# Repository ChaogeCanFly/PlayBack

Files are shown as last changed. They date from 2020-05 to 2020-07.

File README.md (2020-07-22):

# Augmented reality System - Playback
The study of bats requires the ability to record and generate sound waves in the ultrasonic ranges. The required bandwidth for such systems is up to 100kHz, which is much higher than the common acoustic systems designed for humans. Studying bat echolocation capabilities and generating real time acoustic responses requires a minimal latency acoustic system. The few available systems on the market aren`t designed for real time signal processing and manipulation. In order to meet those constrains, a full acoustic system was developed. The system includes a Smart microphone module embedded with a microprocessor, a Speaker-amplifier and a Switch box which is capable of signal redirection and real time processing.
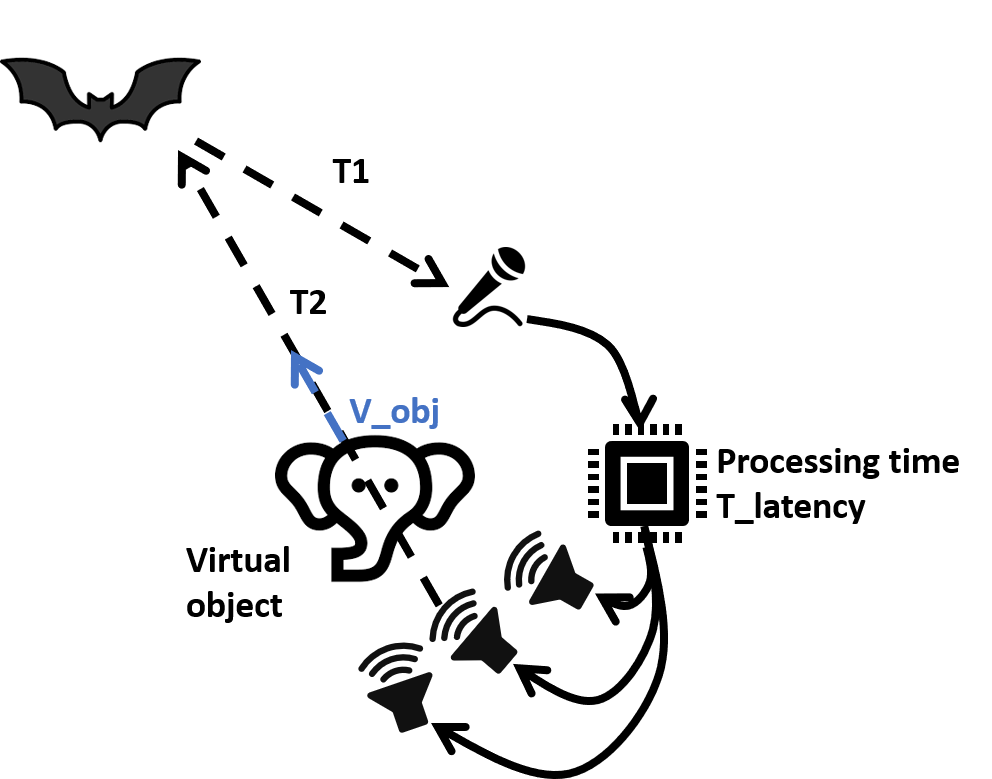
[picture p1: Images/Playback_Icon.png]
Augmented reality illustration

 
## PlayBack
The PlayBack setup consists of three main modules: Smart Microphones, a Switch and speaker amplifiers.  It is designed to monitor audio signals from multiple microphone modules and direct a signal from a selected microphone to an array of speaker modules including DSP options for audio processing in real time. The setup is designed to work at an audio bandwidth of 1-100 kHz at up to 1MS/S.
 
 ### 3d Models:
The casings for the modules have been designed in Fusion 360 and 3d printed
[Microphone](https://a360.co/2HDuYLZ)
[Switch](https://a360.co/36yYfSj)
[Amplifier](https://a360.co/2WX1Lmh)

### System Diagram
The system’s topology is such that the microphone modules are connected to the switch module using a standard RJ25 cable. The 6 wires of the cable are used to pass the following between the Smart microphones and the Switch: power to the module, trigger signal, the audio signal and an analog “quality” signal. The Switch module consists of two MCU`s (Micro Controller Unit), one is used as the Switch interface, and routes the signals while the other is used as a DSP MCU to implement signal processing in real time to the acoustic signal. The speaker amplifiers are connected through an RJ45 cable which in turn is used to supply power from the switch to the amplifiers and transmit the audio signals and the enable signal to the amplifier. The Switch module is connected to a Matlab GUI application running on a PC using an Xbee adapter for wireless operation. In addition, a Saleae logic analyzer is connected to the Switch allowing to monitor the analog signals and the trigger signal.
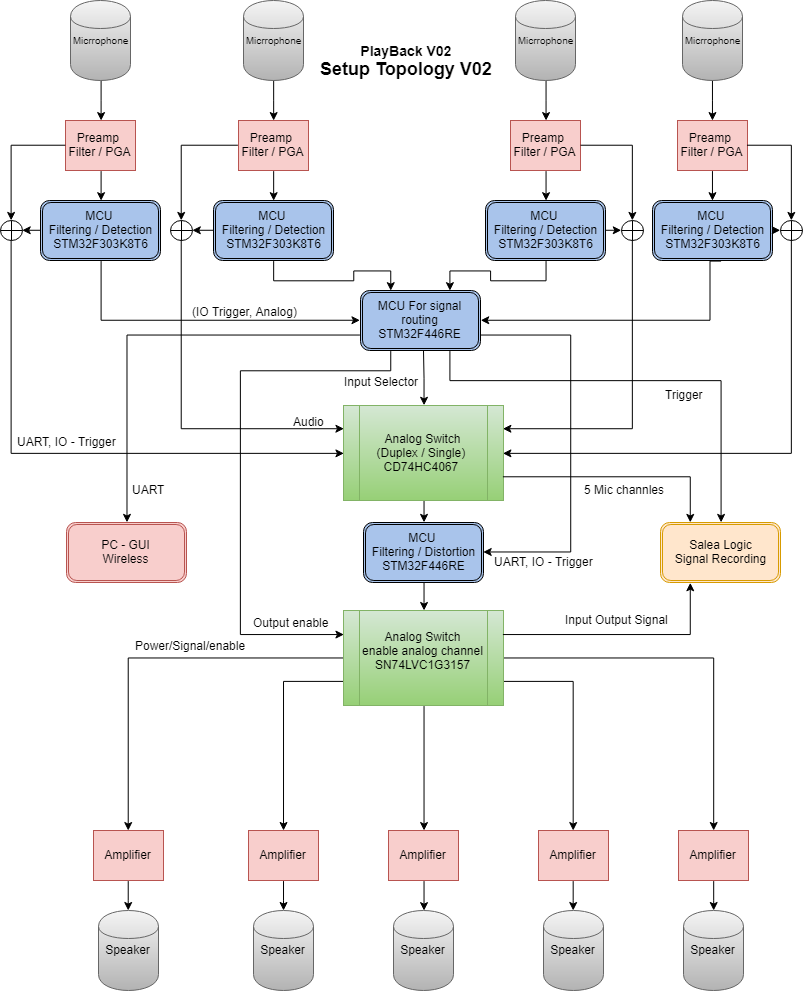
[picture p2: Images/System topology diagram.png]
System Diagram

 
### Smart Microphone
The Smart microphone module is designed to meet the required acoustic bandwidth of bat echolocation calls. In addition, since the system requirements are minimal latency for signal processing and signal manipulation, each of the microphones are embedded with a dedicated microprocessor which is responsible for the initial signal processing of the individual acoustic source. Such an approach allows spreading the computational power required by the system and simplifies the decision-making requirements of the Switch by reducing the acoustic information to a more simplified representation of an acoustic source. i.e. digital triggers / signal quality indication. This approach also allows future expending of the system since each of the microphones acts as an independent entity responsible for its own acoustic system. Adding more microphone to a system will not influence the required signal processing for the main unit.
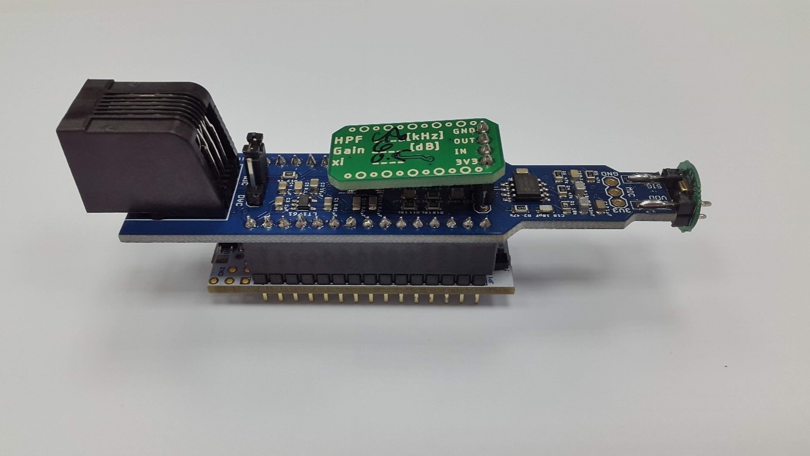
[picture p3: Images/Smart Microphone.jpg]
Smart Microphone


### Switch
The Switch Module is used as the center piece of the system. It connects all the Smart microphone modules and Speaker amplifiers, has an analog routing circuitry to route one of the microphone signals to several speakers. In addition, it acts as a power delivery system, converting a single supply source to several voltage levels for the various components of the system. The switch contains several status indicators such as active speaker LEDs, external trigger. Connectors for all the analog signals running through the system and generally configured status LEDs for future configurations. The switch module contains two MCUs, Switch MCU and DSP MCU, the Switch MCU is used as the system interface and responsible for routing the acoustic signals and monitor the trigger events from the Smart Microphones, while the DSP MCU is used as a DSP and implements various signal processing algorithms.
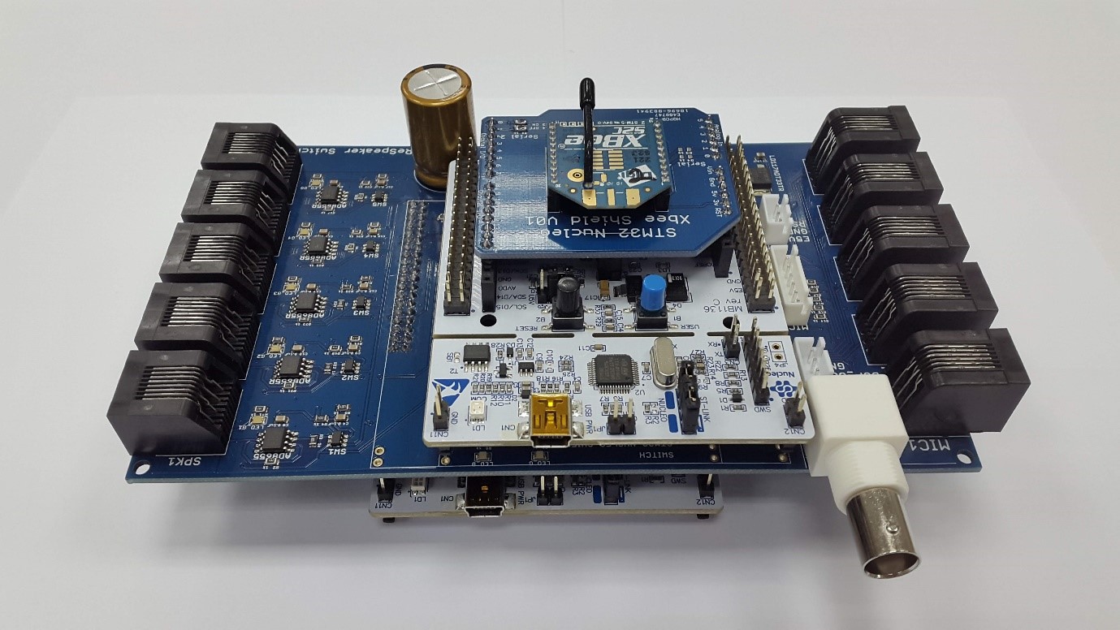
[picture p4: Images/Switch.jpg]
witch
 

### Speaker amplifier
Generating sounds in the ultrasonic frequencies (above 20kHz) requires a dedicated amplifier. Since commercial amplifiers are usually designed for the human hearing range and are commonly implemented through power efficient amplifiers (Class D). These speakers work as digital switches at high frequencies above the human hearing thresholds. The high frequency digital switching is converted to an analog signal using the natural low pass filtering characteristics of the speaker coils. The attempt to use such an amplifier at an ultrasonic frequency will result in high frequency distortions if any sound is generated at all since the common amplifiers are implemented with filters to cut the ultrasonic ranges from the input signals.
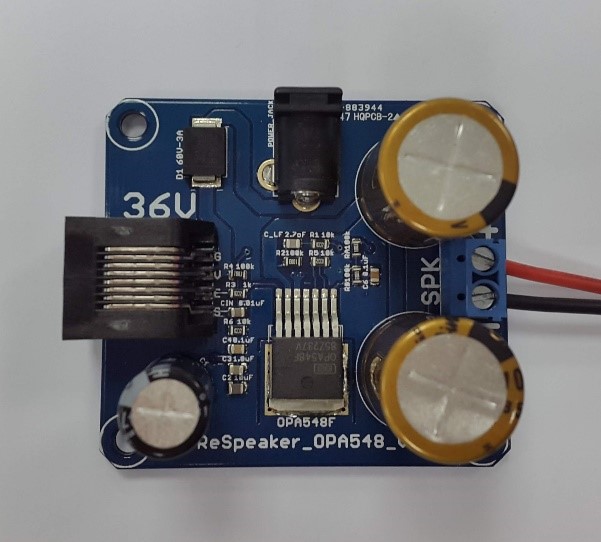
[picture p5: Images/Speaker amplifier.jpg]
Speaker amplifier
 

### GUI Microphone
To control the software parameters of the Smart Microphone, a GUI was created in Matlab. The Microphone has a UART communication over USB with the PC through the MCU`s micro USB connection or through an Xbee adapter board connected to its mate at the PC - as a wireless configuration. The GUI is designed with several section, Connection settings section, Parameters setting and display section, Messages section and Microphone updates section.
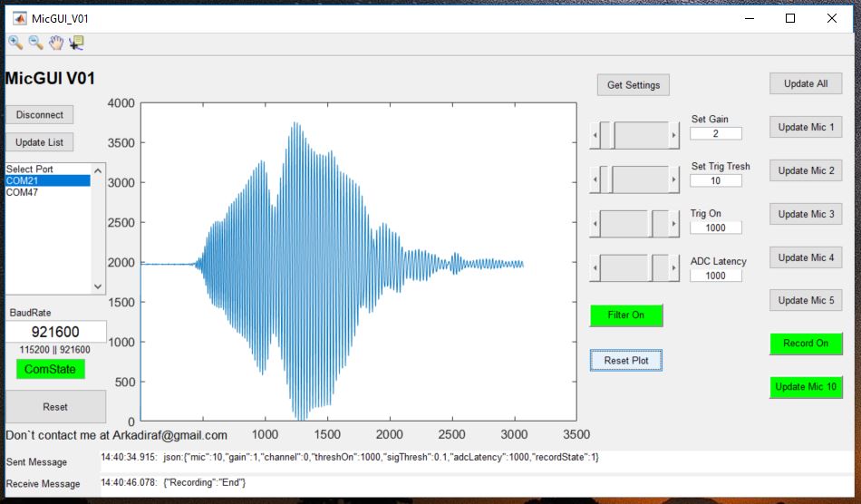
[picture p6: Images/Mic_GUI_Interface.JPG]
GUI Microphone


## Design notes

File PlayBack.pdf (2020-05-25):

# Augmented Reality System for bats based on Acoustic Signal Manipulation

The study of bats requires the ability to record and generate sound waves in the ultrasonic ranges. The required bandwidth for such systems is up to 100kHz, which is much higher than the common acoustic systems designed for humans. Studying bat echolocation capabilities and generating real time acoustic responses requires a minimal latency acoustic system. The few available systems on the market aren`t designed for real time signal processing and manipulation. In order to meet those constrains, a full acoustic system was developed. The system includes a Smart microphone module embedded with a microprocessor, a Speaker-amplifier and a Switch box which is capable of signal redirection and real time processing (Figure 1).

The proposed system in this study allows signal manipulation and processing at up to 1 MHz sample rate with a bandwidth of 1 – 100 kHz. The system is capable of monitoring up to 5 microphones and directing a selected sound source to up to 5 speakers for simultaneous transmission. Several experiments are presented demonstrating the systems capabilities for signal manipulations such as digital filtering, automatic triggering and signal rerouting, inducing latencies and variable gains. In addition, future developments will allow more complex applications such as a real time doppler effects.

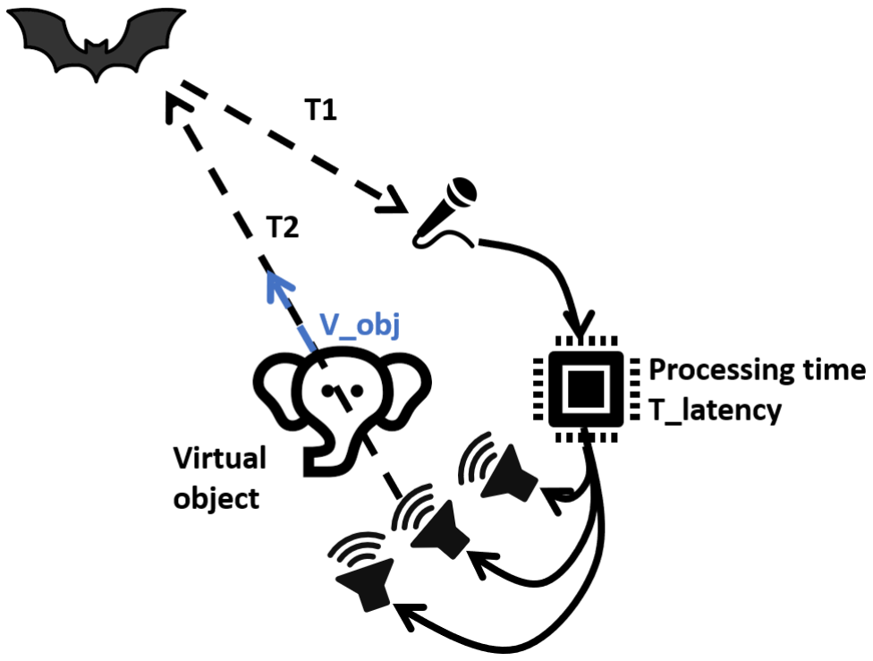
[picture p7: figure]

Figure 1. Augmented reality illustration: A bat call is received by a microphone, processed and transmitted through several speakers generating a virtual object to be perceived by a bat.

## 1 System Overview

The PlayBack setup consists of three main modules: Smart Microphones, a Switch and speaker amplifiers (Figure 2). It is designed to monitor audio signals from multiple microphone modules and direct a signal from a selected microphone to an array of speaker modules including DSP options for audio processing in real time. The setup is designed to work at an audio bandwidth of 1-100 kHz.

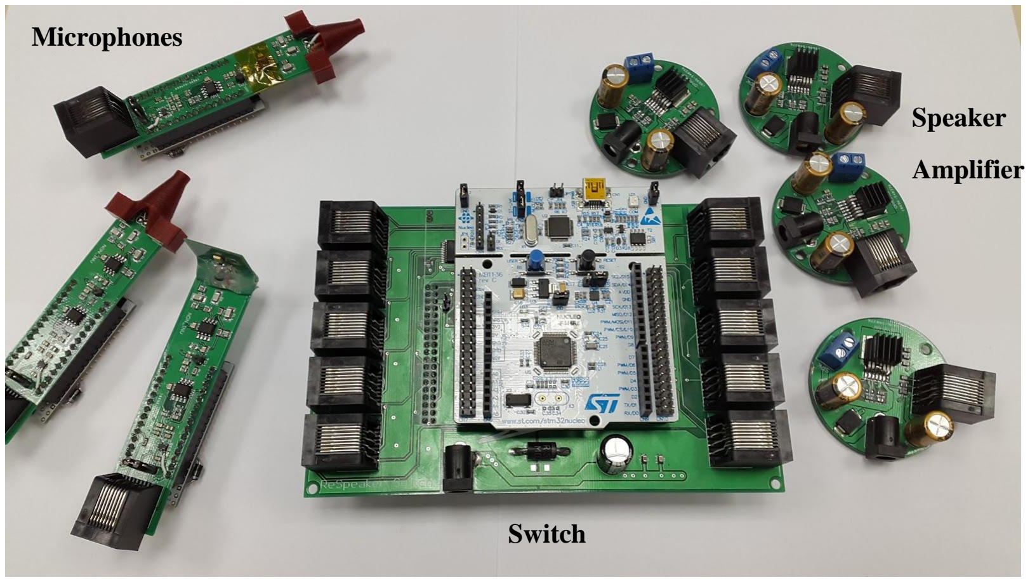
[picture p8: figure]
Microphones; Switch; Speaker; Amplifier

Figure 2. The Playback system – Smart Microphone on the left, Switch Module in the middle and Speaker amplifiers on the right.

The system’s topology (Figure 3) is such that the microphone modules are connected to the switch module using a standard RJ25 cable. The 6 wires of the cable are used to pass the following between the Smart microphones and the Switch: power to the module, trigger signal, the audio signal and an analog “quality” signal. The Switch module consists of two MCU`s (Micro Controller Unit), one is used as the Switch interface, and routes the signals while the other is used as a DSP MCU to implement signal processing in real time to the acoustic signal. The speaker amplifiers are connected through an RJ45 cable which in turn is used to supply power from the switch to the amplifiers and transmit the audio signals and the enable signal to the amplifier. The Switch module is connected to a Matlab GUI application running on a PC using an Xbee adapter for wireless operation. In addition, a Saleae logic analyzer is connected to the Switch allowing to monitor the analog signals and the trigger signal (Figure 4).

Figure 3. System topology diagram: An array of up to 5 microphone modules are connected to a switch module which connects to up to 5 speaker amplifier modules with ultrasonic speakers. The switch module is connected to a PC and the signals are monitored by a Saleae Logic analyzer.

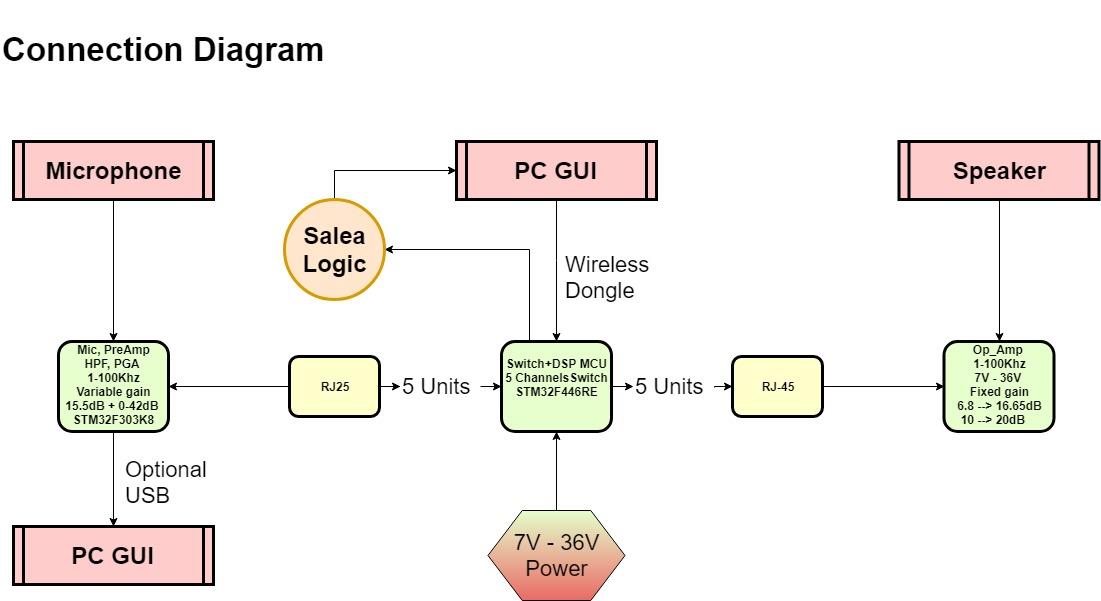
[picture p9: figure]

Figure 4. Playback System Connection diagram: Microphones connected through RJ25 cables to a switch module which is connected to speaker amplifiers through RJ-45 cables.

## 1.1 The smart microphone

The Smart microphone module (Figure 5) is designed to meet the required acoustic bandwidth of bat echolocation calls. In addition, since the system requirements are minimal latency for signal processing and signal manipulation, each of the microphones are embedded with a dedicated microprocessor which is responsible for the initial signal processing of the individual acoustic source. Such an approach allows spreading the computational power required by the system and simplifies the decision-making requirements of the Switch by reducing the acoustic information to a more simplified representation of an acoustic source. i.e. digital triggers / signal quality indication. This approach also allows future expending of the system since each of the microphones acts as an independent entity responsible for its own acoustic system. Adding more microphone to a system will not influence the required signal processing for the main unit.

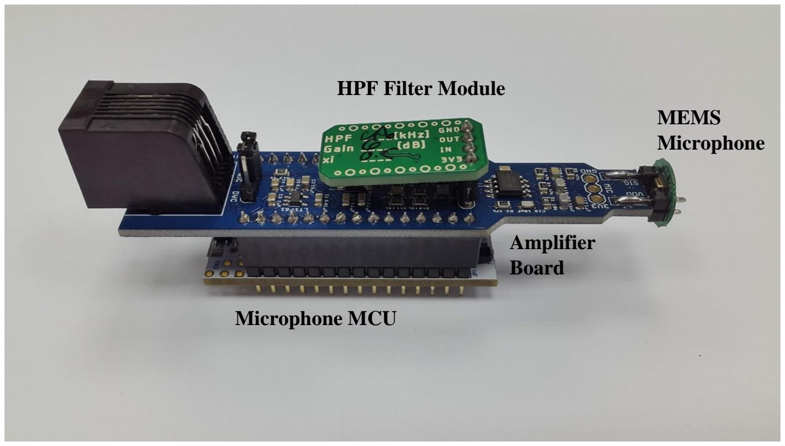
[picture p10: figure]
HPF Filter Module; Microphone MCU; MEMS Microphone; Amplifier Board

Figure 5. The Smart Microphone module: Round PCB populated with a mems microphone membrane, attached to an analog amplifier board (blue PCB). At the top attached an analog HPF filter module and at the button an MCU board.

### 1.1.1 Electronics

The Smart Microphone module is assembled by 4 independent electronic boards (Figure 5). The modules contain several parts, an analog mems membrane for the ultrasonic ranges and an analog amplifier board matched for the mems microphone. The amplifier board contains an adapter for an Analog high pass filter to allow the replacements of the board for various filter characteristics for the specific acoustic responses required. The whole system is mounted on a microcontroller board for signal detection and signal manipulation.

The circuit components were chosen to meet the system’s requirements of an audio bandwidth of 1-100kHz. The mems microphone (SPU0410LR5H) chosen for the design has an acoustic characteristic at up to 100kHz. The signal operational amplifiers (Op Amp`s)

chosen for the design are an AD8655 which is a low noise high bandwidth operational amplifier, with 28MHz bandwidth, capable of a single supply design and rail to rail signals. The programmable gain amplifier (PGA - PGA112) module has similar analog characteristics of 10MHz bandwidth, rail to rail signals and is compatible for single supply designs. In addition, the PGA has an internal MUX of 2 channels, allowing a digital selection of the signal source. The chosen PGA is cable of an additional amplification stage in binary stages from 1 to 128 gain. The main board 3V3 LDO regulator LT1761 is selected for its good noise rejection for the circuit`s analog bandwidth.

In order to work with an analog microphone a matching amplification circuit is implemented. The amplification circuit has several stages each selected and implemented for its individual purpose and are illustrated in Figure 6. The first stage contains an amplifier circuit at a non-inverting configuration with a gain of 15.1dB and is called a preamplifier. It`s purpose is to amplify the “weak” signals generated by an analog microphone. It is designed with a high impedance input to match the high impedances of the analog microphone. The amplification is selected to meet the full bandwidth of the microphone up to its saturation point. Following the preamplifier is an analog high pass filter module (HPF module). The analog high pass filter is implemented on a separated board in order to be easily replace by a different high pass filter module with different analog characteristics. Following the HPF module is a programmable gain amplifier (PGA). The PGA is configured digitally by the on board MCU and as an internal mux allowing the selection of a filtered signal from the HPF module or the unfiltered signal fed directly by the preamplifier. The PGA acts a variable gain amplifier and is implemented in order to amplify the signals to the full scale of the microprocessor’s ADC levels (analog to digital converter) by that utilizing the full resolution of the MCU ADC which is limited to 12bit. The amplifier board has a physical jumper which can select the output source for the acoustic signal. Either the generated signals by the MCU, or the analog signal of the PGA unit.

The HPF module for the setup is designed as a second order analog high pass filter at a cutoff frequency of 48kHz with a damping factor of 0.5 in addition it adds a 6dB gain to the signal respectively to the dumping factor, The design was evaluated using a Simulink simulation and evaluated based on preliminary recording for best performance at ultrasonic ranges of a bat callings.

The amplifier board is mounted on top of a microprocessor which samples the amplified signals of the PGA unit and generates an analog signal through its digital to analog converter (DAC) at 12bit resolution and up to 1 MHz sample rates. The MCU can delay the signals and detect signals presence by amplitude threshold evaluation. When a signal is present an IO interrupt is set to notify the switch of a present signal. The software parameters of the MCU are configured by a Matlab GUI (Figure 9, Figure 6).

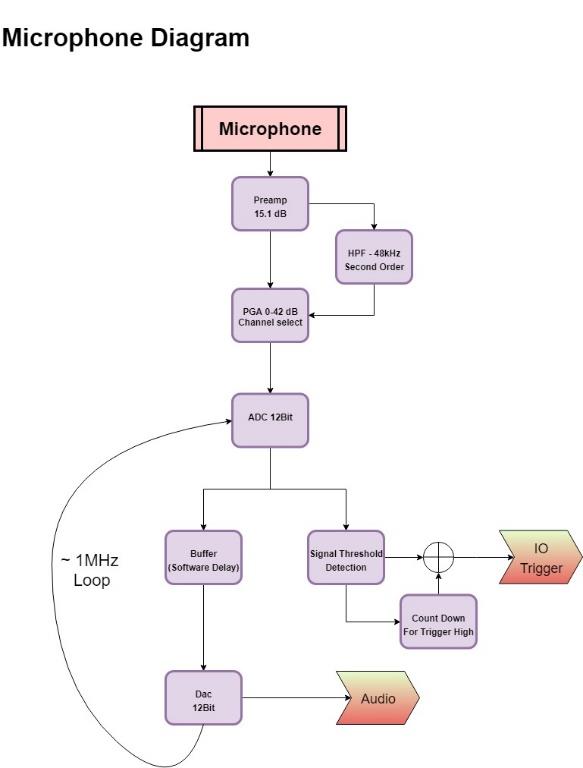
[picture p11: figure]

Figure 6. Smart Microphone diagram: Hardware & Software implementation diagram. Illustrated an amplifier circuit, with preamp, HPF and PGA implementation. Following sampling of the signal by a microcontroller, and software implementation for the sample. Signal detection, and delay implementation. With appropriate signal generation – i.e. Digital trigger and generated analog signal.

### 1.1.2 MCU code

The code for the Smart Microphone MCU (STM32F303) is implemented through an STM32CubeIDE environment, using C++ language. The MCU is responsible to the communication with the Matlab GUI and implements some signal processing in real time.

The main code algorithm is represented in Figure 6, The MCU performs an analog to digital conversion at 12 bits resolution (ADC), stores the sample into a circular buffer, checks if a bat signal is present by a simple threshold comparison to a stored variable, if a signal is present the MCU sets a trigger IO high to update the Switch MCU of a present signal and sets a countdown which ends with resetting the trigger IO state. A digital to analog conversion

(DAC) at 12 bits is than performed to a stored value in the circular buffer, defined by the set delay. The whole loop is performed at about 1MHz.

The communication with the Matlab GUI is done through a UART stream which triggers an interrupt routing in the MCU workflow. The incoming byte is checked for the correct values depending on the defined state for the transmission (Figure 7).

- State 1: compares the incoming byte to the defined header - failed comparison resets the buffer and transmission state
- State 2: stores the incoming bytes to a packet stream.
- State 3: compares the incoming byte to the defined footer - failed comparison resets the buffer and transmission state.

When a successful transmission is performed, the defined packet bytes are parsed in the format of a Json message. The variables are derived by the variable names and used to update the stored variables of the MCU in the virtual EEPROM memory of the MCU. The data exchange is completed by sending an acknowledgement message to the Matlab GUI, stating the microphone number using the Json format for message construction.

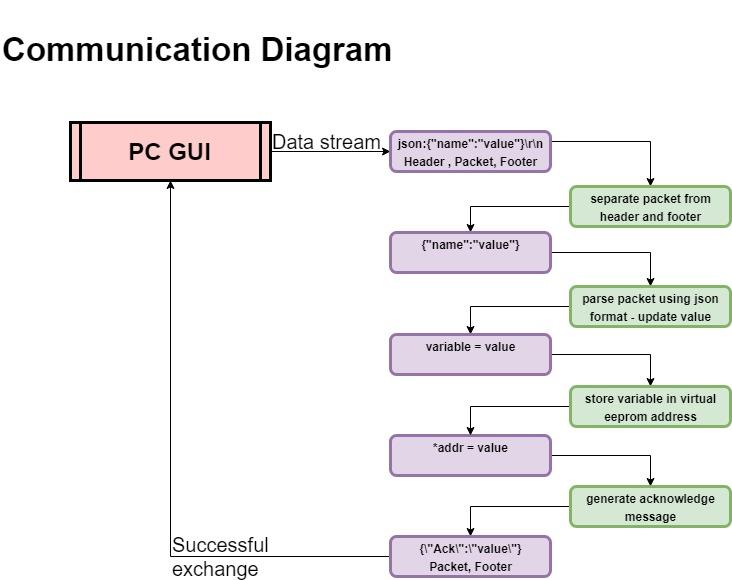
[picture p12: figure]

Figure 7. Smart Microphone communication diagram: The implementation of the communication protocols is based on packet handling and json formats.

Recoding of a signal is performed when a recording state is selected in the Matlab GUI. The transmission begins when a countdown for the trigger event is finished. The recorded signal is then transmitter in a binary form (Figure 8). Prior to sending the packet, an update is sent in a json format to notify the Matlab GUI of an upcoming binary packet, the size of the binary packet, and an index for the start of the circular buffer. The Matlab GUI is then switched to the binary packet retrieval state and the MCU sends the circular buffer in a binary format. After the binary packet is transmitted, the MCU sends a json message stating the end of a transmission and by that it acknowledges the Matlab GUI of a successful packet transfer. Using a binary format, reduces significantly the number of bytes required to be transmitted and the overhead for the communication protocol over UART, allowing a continuous capture of bat calls at up to 20 – 30 calls a second at a 3-4 ms duration each.

Figure 8. Binary packet transfer: Binary communication protocol allows large files with minimal bandwidth requirements, including an error detection mechanism implemented by a handshake implementation.

### 1.1.3 Matlab GUI

To control the software parameters of the Smart Microphone, a GUI was created in Matlab (Figure 9). The Microphone has a UART communication over USB with the PC through the MCU`s micro USB connection or through an Xbee adapter board connected to its mate at the PC - as a wireless configuration. The GUI is designed with several section, Connection settings section, Parameters setting and display section, Messages section and Microphone updates section.

The Matlab GUI buttons settings include:

Disconnect / Connect – Disconnect from currently connected USB COM Port. Or connect to the selected COM Port from the Select Port menu.

Update – Refreshes the Select Port menu with the available COM Ports connected to the MCU.

Select Port Menu – Displays the available COM Ports connected to the PC.

BaudRate – Baud Rate for the selected connection, for a Cable connection the configured baud rate is 921600, as for the wireless configuration it is 115200.

ComState – Displays the connection status with the MCU, Green if the connection is active, Red for an inactive connection.

Reset – Resets the GUI configuration and updates the MCU with the default configuration settings.

Sent Message – Displays the last sent messages to the MCU.

Received Message – Displays the last received message from the MCU.

Plot Frame – Displays the received buffer from the MCU.

Get Settings – Retrieves the setting stored at the MCU and updates the GUI configuration to match those settings.

Set Gain – Gain settings to the PGA module, from 1- 128 with binary scale. Connected to the slide bar next to it and refreshes the value / slide bar based on whichever is used.

Set Trig Tresh – Sets the trigger threshold values from 1-100 in %. Connected to the slide bar next to it and refreshes the value / slide bar based on whichever is used.

Trig On – Sets the number of samples used to maintain a trigger at high state after trigger event. Connected to the slide bar next to it and refreshes the value / slide bar based on whichever is used.

ADC Latency – Sets the number of samples to delay the signal. Connected to the slide bar next to it and refreshes the value / slide bar based on whichever is used.

Filter On – Changes the Filter Status. Filter On – Green, Filter Off – Gray.

Reset Plot – Resets the Plot window from the accumulated received buffer.

Update All – Update whichever microphone that is connected to the GUI with the current settings displayed by the GUI. Turns Green for successful update, Red for a failed update attempt.

Update Mic 1-5, 10 – Updates the specifically numbered microphone if connected to the GUI with the current settings displayed by the GUI. Turns Green for a successful update, Red for a failed update attempt.

Record On – Sets the Recording state. Record On – Green, Record Off – Gray. When recording is enabled, recorded data transmitted to the GUI will be updated over the Plot window.

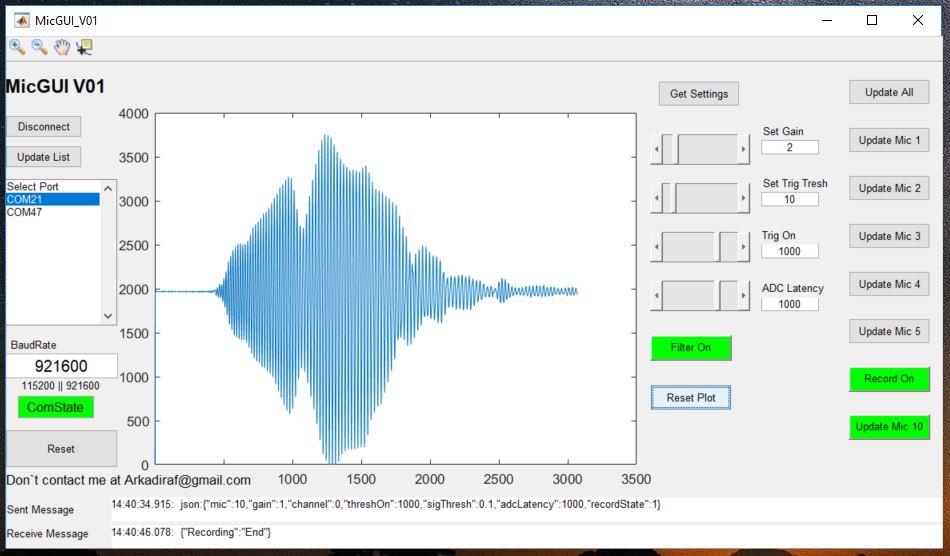
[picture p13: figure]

Figure 9. Smart Microphone Matlab GUI: includes various button and slides to manipulate the software behavior of the microphone MCU. With visual representations of the microphone configuration and plot of the acoustic signals as recorded by the Smart microphone MCU.

### 1.1.4 Casing

The casing for the microphone has been designed in Fusion 360 and 3d printed, Figure 10. The casing has a switchable cover for the microphone in order to test covers which may implement some signal direction. In addition, various adapters have been designed to accommodate various setup options.

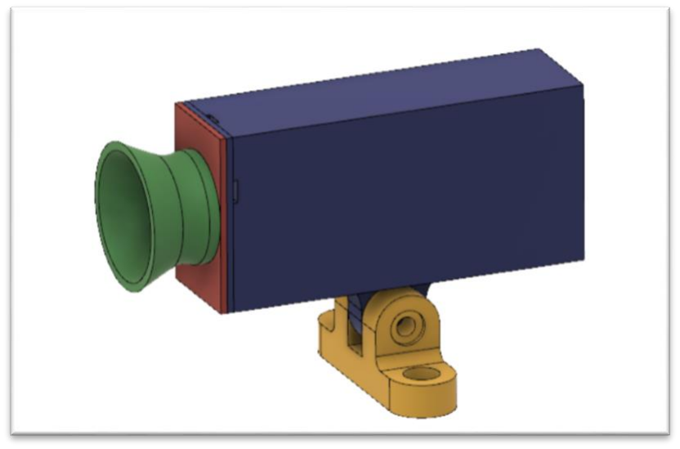
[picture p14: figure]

Figure 10. 3d model for the Smart Microphone module: Designed in Fusion 360 for 3d printing fabrications. Simple robust design to protect and ease the use of the electronics.

## 1.2 Switch module

The Switch Module is used as the center piece of the system. It connects all the Smart microphone modules and Speaker amplifiers, has an analog routing circuitry to route one of the microphone signals to several speakers. In addition, it acts as a power delivery system, converting a single supply source to several voltage levels for the various components of the system. The switch contains several status indicators such as active speaker LEDs, external trigger. Connectors for all the analog signals running through the system and generally configured status LEDs for future configurations. The switch module contains two MCUs, Switch MCU and DSP MCU, the Switch MCU is used as the system interface and responsible for routing the acoustic signals and monitor the trigger events from the Smart Microphones, while the DSP MCU is used as a DSP and implements various signal processing algorithms (Figure 11, Figure 12).

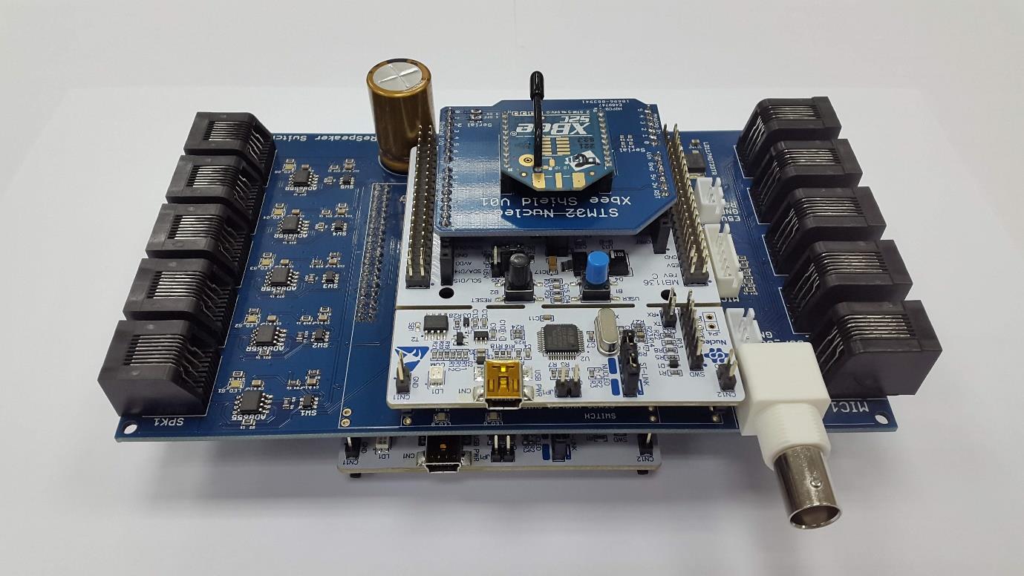
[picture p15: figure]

Figure 11. Switch Module: contains 2 MCU, DSP MCU for signal processing, and Switch MCU for signal routing. The base board is design for analog signal routing with several status indicators external triggers and power handling.

### 1.2.1 Electronics

The Switch Contains several sections on the board. Power delivery, Signal routing, Signal monitoring. The power delivery section is designed to work with supply voltages of 7 - 36V at 5A limit. It has a reverse polarity protection diode, a DC-DC converter module (D24V50F5) to generate 5V from the supply voltage. The generated 5V is used to feed the MCU`s present on the Switch and the connected Smart Microphones. In addition, the 5V is regulated to 3V3 level using a linear regulator (LD117ADT33TR) for better noise rejection. The 3V3 Regulated voltage is used for the analog circuit of the board. In addition, the supply voltage is directed to the Speaker amplifiers through the reverse polarity protection diode.

The acoustic signal is routed using a multiplexer integrated circuit (MUX IC), the MUX (CD74HC4067SM96) is controlled by the Switch MCU, it selects one of the acoustic signals arriving from the connected Smart Microphones and routes the signal to the DSP MCU. The generated signal from the DSP MCU is routed to the analog switches (741G3157DBVR) allowing the selection of multiple speakers for the same input signal. In order to eliminate cross talk between the speaker amplifiers. the signals are buffered by an operations amplifier (OP AMP, AD8655),

The Switch MCU is a Nucleo-STM32F446 it monitors the trigger events arrived from the Smart Microphones. In addition, it has trigger event monitor from the DSP MCU (Nucleo-STM32F446) which is used for DSP frequency loop calculation. Several status LED indicators are present on board, and an external trigger connector is present. Several of the signals are optionally connected to an external hardware for farther monitoring. Such as the Trigger Signal, Smart Microphones analog signal, selected microphone signal and generated signal.

The Switch MCU has an Xbee adapter allowing a wireless connection to the PC and has an internal UART connection with the DSP module for passing messages to and from the DSP MCU and the PC GUI. The externally monitored signals are connected to a SALEAE logic analyzer, capable of logging up to 8 analog signals at 12bit resolution (at -10V to 10V range).

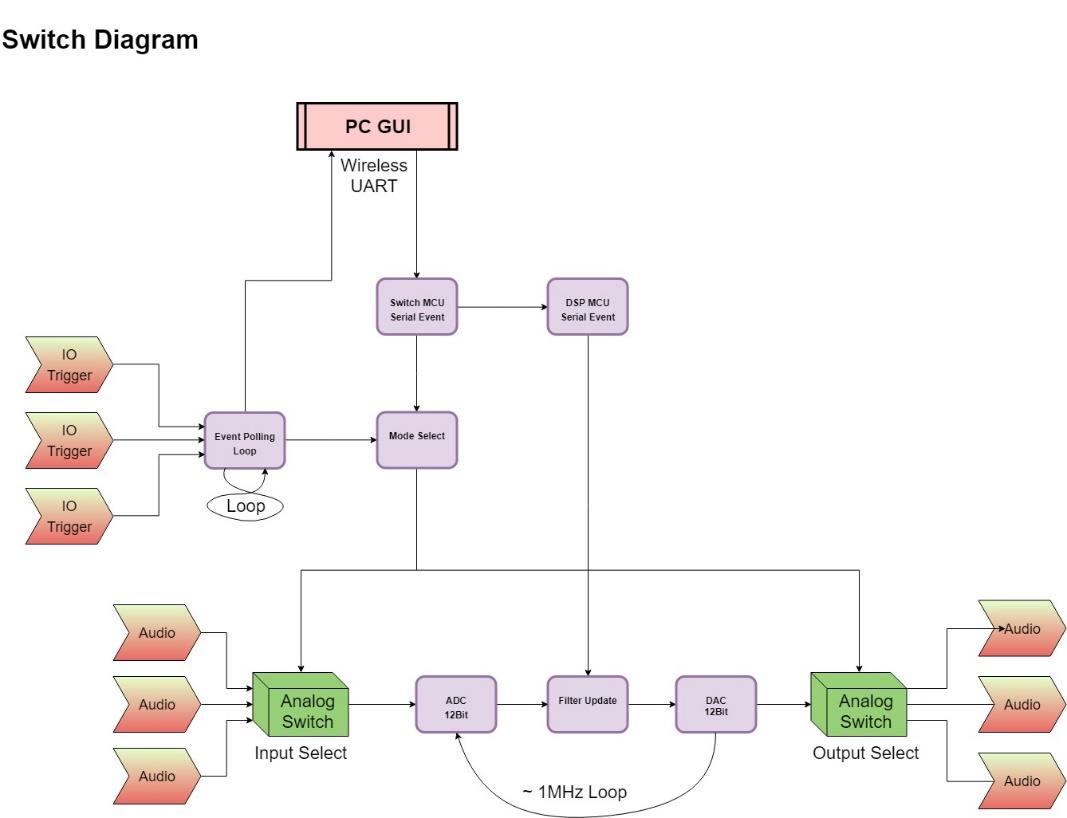
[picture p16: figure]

Figure 12. Switch Diagram: illustrates Software & Hardware implementations for the Switch board with both microcontrollers present on the Switch module.

### 1.2.2 MCU code

The code for the Switch module is implemented through Mbed IDE environment, using C++ language. The Swith MCU (STM32F446) is responsible of the communication with the Matlab GUI and performs signal routing and monitoring. While the DSP MCU (STM32F446) performs the signal processing in real time Figure 12.

The main loop of the DSP MCU performs an analog to digital conversion (ADC) at 12 bits resolution. Following a signal manipulation based on the configured modes:

Off – Sets the acoustic signal to output 0.

Passthrough – Outputs the sample signal without any modification using a 12 bits DAC.

High Pass – Performs a high pass filter using the configured coefficients and the defined order, in the format of IIR Butterworth Filter, implemented as a direct form 1 configuration. Applies a digital gain to the signal and outputs the signal using a 12 bits DAC.

High Pass + Trigger – Performs a high pass filter like the high pass mode and checks for a present bat call based on a simple threshold detection comparison with a pre-defined value. When a successful event is detected a countdown is set with a predefined length which ends with a period of disabling the output signals in order to disable resonance effects caused by the signal echoes with itself. While no event is detected, or the countdown hasn’t ended the output signal is generated using a 12 bits DAC.

High Pass + Trigger + Gains - performs similar operations to the High pass + Trigger mode but with a difference of changing the digital gain between signal detection based on a predefine gain vectors.

The main loop frequency is changed by the amount of computation is required at each of the applied modes, the most significant influence is the filter order. The frequency may change as far from 500kHz to 5MHz. The frequency of the loop is measured from the toggle of an event IO shared by the Switch MCU during each 10e6 iteration of an event loop.

The Switch MCU main function is to monitor the signal events supplied by the Smart Microphones and rout the signals as set by the configured mode.

- Manual Operation – Set the MUX by the to the define microphone by the Matlab GUI and enables the defined speaker amplifiers as defined by the Matlab GUI.
- Auto Operation – Switches the MUX automatically from the events triggered by the Smart Microphone and enables the speaker amplifiers by the same event. I.E – for an event from Smart Microphone on channel 1. The signal is routed from channel 1 and speaker amplifier 1 is set to on while the rest are disabled.

In addition, the Switch MCU is responsible to the communication with the Matlab GUI as represented in Figure 13. The communication with the Matlab GUI is done through a UART stream which triggers an interrupt routing in the MCU workflow. The incoming byte is checked for the correct values depending on the defined state of the transmission.

- State 1: compares the incoming byte to the defined header - failed comparison resets the buffer and transmission state
- State 2: stores the incoming bytes to a packet stream.

- State 3: compares the incoming byte to the defined footer - failed comparison resets the buffer and transmission state.

When a successful transmission is performed, and a defined packet byte are parsed in the format of a Jason message. The variables are derived by the variable names and used to configure the Switch operation. The data exchange is completed by sending an acknowledgement message to the Matlab GUI. IF the destination packet is set to the DSP MCU the message is streamed over the shared UART with the DSP MCU and in turn the DSP MCU performs stream detection and packet parsing with acknowledge message generation which in turn is stream back to the Matlab GUI through the Switch MCU.

Figure 13. Switch Communication diagram: Illustrates the implemented communication protocol between the Matlab GUI and both microcontrollers. Demonstration of packet handling and routing.

### 1.2.3 Matlab GUI

To control the software parameters of the Switch a GUI was created in Matlab (Figure 14). The Switch MCU is connected to the GUI using UART communication over Xbee with an Xbee adapter connected to a PC as a wireless configuration. The GUI is designed with several section, Connection settings section, Messages section, Switch control settings section, DSP setting control section and events monitoring section.

The Matlab GUI buttons settings:

Disconnect / Connect – Disconnect from currently connected USB COM Port. Or connect to the selected COM Port from the Select Port menu.

Update – Refreshes the Select Port menu with the available COM Ports connected to the MCU.

Select Port Menu – Displays the available COM Ports connected to the PC.

BaudRate – Baud Rate for the selected connection, default at 57600 for the wireless configuration.

ComState – Displays the connection status with the MCU, Green if the connection is active, Red for an inactive connection.

Reset – Resets the GUI configuration and updates the MCU with the default configuration settings.

Debug Mode – Enables / Disable debug messages.

Sent Message – Displays the last sent messages to the MCU.

Received Message – Displays the last received message from the MCU.

Debug Message – Displays the last received debug message from the MCU.

Microphone Select – Allows manual selection of the microphone, for Autonomous mode the selection automatically updates based on the Automatically selected mode by the MCU.

Speaker Select – Allows manual selection of the enabled speakers, for Autonomous mode the selection automatically updates based on the Automatically selected mode by the MCU.

Mode Select – Allows the selection of the DSP operation mode.

Off Mode – Sets the output signal of the DSP MCU to VCC/2.

Passthrough – Sets the output signal of the DSP MCU to its input.

Highpass – Applies IIR HPF filter to the input signal based on the latest HPF parameters.

HPF + Trigger – Applies IIR HPF filter to the input signal based on the latest HPF parameters and implement signal trigger effect.

Gains + Trigger – Applies IIR HPF filter to the input signal based on the latest HPF parameters and implement signal trigger effect with variable gains between the triggers.

TBD – Future mode.

Loop Freq [ kHz] – Displays the measured frequency loop of the DSP MCU

Off On (Loop Freq) – Enables / Disables the measuring of the frequency loop of the DSP MCU

Set Gain – Applies a digital gain to the signal, Valid to modes implementing HPF.

Set Trig Tresh – Sets the trigger threshold detection, valid values 1-100 in %. Connected to the slide bar next to it and refreshes the value / slide bar based on whichever is used.

Set Trig Pass – Sets the number of samples to pass after trigger event. Connected to the slide bar next to it and refreshes the value / slide bar based on whichever is used.

Set Trig Pause – Sets the pause time in ms after trigger event implementation. Connected to the slide bar next to it and refreshes the value / slide bar based on whichever is used.

Update Param – Sends an update to the DSP MCU with the updated setting.

Get Settings – Retrieves the settings of the GUI from memory.

Save Settings – Saves the settings of the GUI to memory.

Microphone Events – Displays the received event from the Smart Microphones. Mic column displays the Microphone number which has triggered the event, time column displays the time event for the trigger as measured by the Switch MCU.

Save Log – Saves the microphone events log to memory using a file name written below the button.

Play Sound – Plays a Stored audio file in the DSP MCU memory and generates a trigger event prior playing the file.

Operation Mode – Switches the operation mode of the Switch MCU between Manual and Auto

Filter order – Sets the IIR HPF filter order for the filter design.

Cut Off Freq [kHz] – Sets the IIR HPD filter cut off frequency in kHz for the filter design.

Design Filter – Designs an IIR high pass filter using the defined Filter Order and Cut Off frequency parameters and displays the frequency response plot using the Matlab DSP toolbox. The filter data stored as a SOS matrix.

Update DSP – Sends the latest filter coefficients to the DSP MCU designed by the filter design and stored as a SOS matrix.

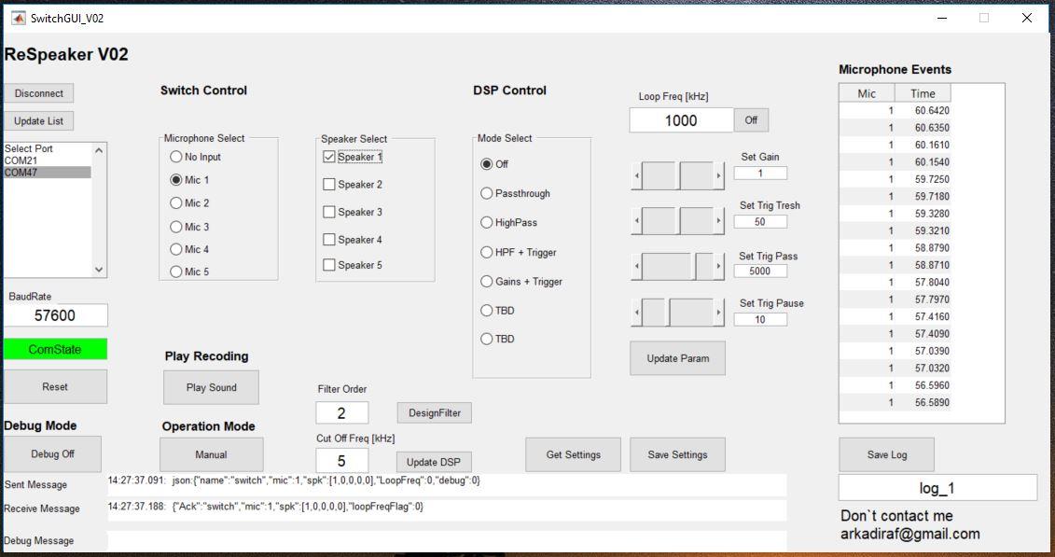
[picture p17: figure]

Figure 14. Switch Matlab GUI: Includes various buttons and status indicators. Allows easy manipulation of the software implemented on the Switch microcontrollers.

### 1.2.4 Casing

The casing for the Switch has been designed in Fusion 360 and 3d printed (Figure 15). The casing has various embedded text in order to indicate important information to the user such as power connection, iteration, connectors, led indicators, flashing ports etc.

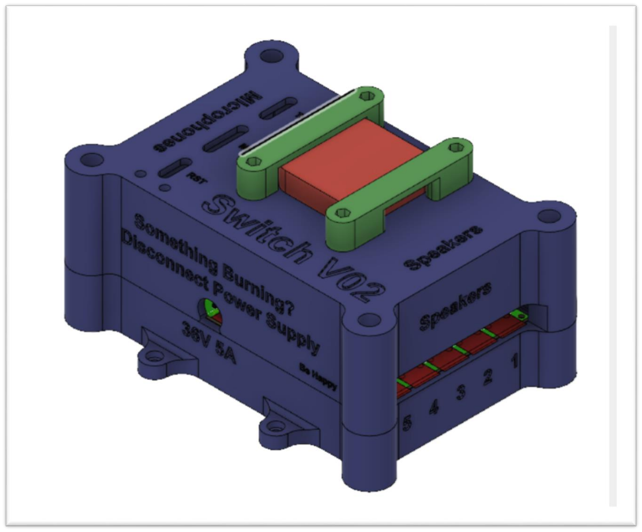
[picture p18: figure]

Figure 15. 3D model of the Switch module: Designed in fusion 360 for 3D printing fabrication. The design allows protection and eases the handling of the designated electronics.

## 1.3 Speaker amplifier

Generating sounds in the ultrasonic frequencies (above 20kHz) requires a dedicated amplifier. Since commercial amplifiers are usually designed for the human hearing range and are commonly implemented through power efficient amplifiers (Class D). These speakers work as digital switches at high frequencies above the human hearing thresholds. The high frequency digital switching is converted to an analog signal using the natural low pass filtering characteristics of the speaker coils. The attempt to use such an amplifier at an ultrasonic frequency will result in high frequency distortions if any sound is generated at all since the common amplifiers are implemented with filters to cut the ultrasonic ranges from the input signals.

To overcome these constrains, a speaker amplifier module has been developed (Figure 16). The speaker amplifier board contains a power amplifier circuit designed for high frequency audio signals at the range of 1-100 kHz which supports up to 36V and 3A. It is designed around a Class A/B amplifier (Analog power amplifier) for a 4ohm tweeter speaker such as a ScanSpeak R2004 or a Tymphany XT25SC90 speaker.

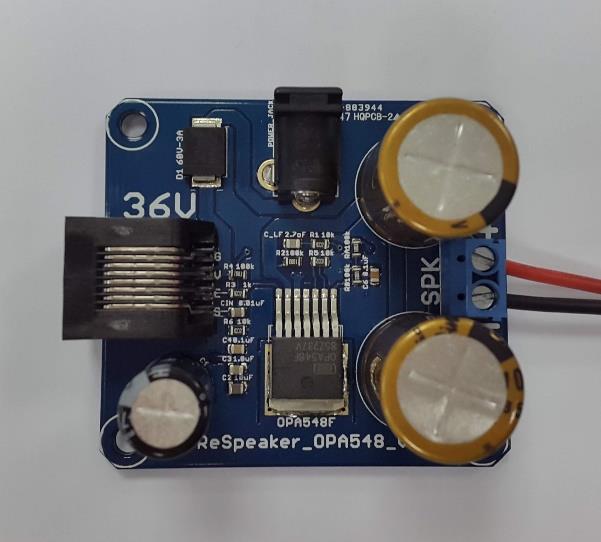
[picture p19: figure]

Figure 16. Speaker amplifier module: designed for single supply and meets the required bandwidth of the system.

### 1.3.1 Electronics

The speaker amplifier module is designed around the OPA548F power amplifier, which has a bandwidth of 1MHz, and can work at up to 5A. The amplifier implementation is for a single supply operation, valid for 5-36V supply voltages, the power can be supplied through a Power jack present on board or through the RJ45 cable connected to the Switch. The circuit has a constant gain setting implemented as an inverting amplifier and is set based on the desired operation. In addition, a current limit is set to 3A, and the circuit has an enable optioned which is controlled by the switch module.

### 1.3.2 Casing

The casing for the Speaker and speaker amplifier has been designed in Fusion 360 and 3d printed (Figure 17). The Speaker casing has a removable cover in order to implement sound directionality. In addition, various adapters have been designed to accommodate various setup options.

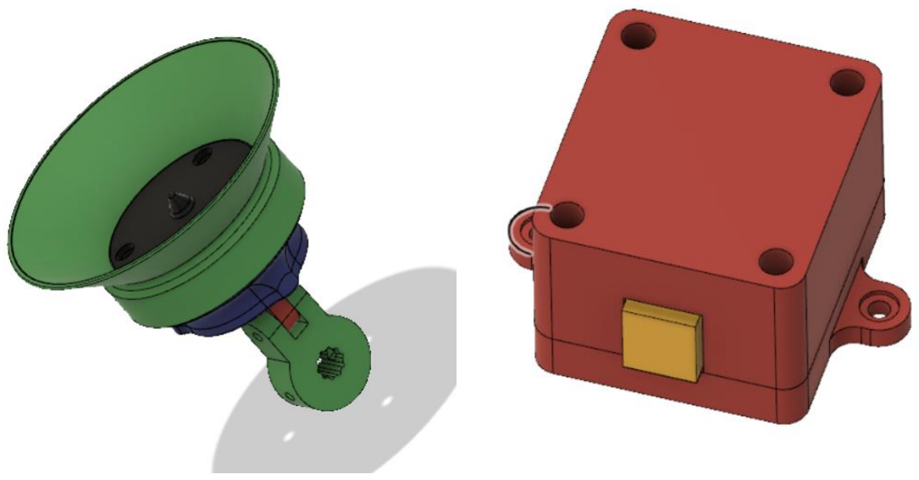
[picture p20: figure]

Figure 17. Speaker and speaker amplifier casings: designed in fusion 360 for 3d fabrication. The casing protects the circuit boards and allows mounting of various 3d printed acoustic focus – cone element.

## 2 Results

To evaluate the performance of the system and test its fitness to work with bats, a series of experiments were conducted. Ex.1 Evaluates the system`s frequency response. While Ex.2 though Ex.7 Evaluates various modes of operations. To conduct the experiments two experimental setups were established. One is a simplified setup consisting of 2 microphones and one speaker (Figure 18); and the other is a full-scale setup consisting of 5 microphones and 5 speakers (Figure 19). For the experiments, the system was powered by a Lithium polymer battery pack at 11V (3s Battery). The system’s output signals were recorded by a Saleae logic analyzer. The Saleae logic analyzer was set to initiate recordings by a trigger pulse from the Switch MCU at a recording frequency 3.125MHz. The Saleae Logic analyzer recorded the 5 Microphone channels, the DSP MCU input and output and the trigger event channel from the Switch MCU.

In addition to the system setup, a Chirper box was used. The Chirper box, which was designed for this project, is a simplified version of the playback system, based on one MCU (STM32F466) connected to an amplifier, with a state button to set the output on and off, and a potentiometer to set the repeatability of the recorded signal on the MCU flash memory.
The chirper box acts as a virtual bat box allowing the simulation of a bat call without using an actual bat for the performance test experiments. For the Chirper box, two recordings were prepared, one of a bat call recorded by a GRAS calibrated microphone, and the other is a simulated chirp signal consisting a frequency sweep from 1-100kHz. The chirper box is powered by an external Power bank battery for mobility, allowing to freely move it in the room.

Figure 18. Experiments setup 1: 2 microphones on the left connected to a switch box in the middle, with 1 speaker module on the right. Battery powered setup. On the right a Chirper box. Right figure:

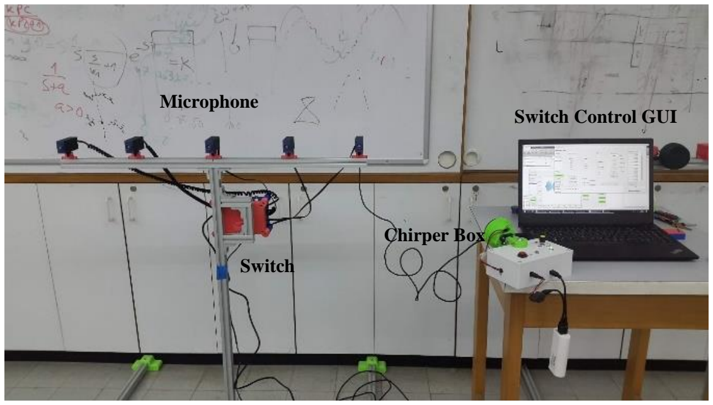
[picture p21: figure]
Microphone; Switch; Chirper Box; Switch Control GUI

FIGURE 19. Experiment setup 2: 5 microphone modules mounted on a linear rail and connected to a switch box, a laptop running a microphone control GUI, Switch control GUI, Saleae logic analyzer recording GUI. Chirper Box.

## 2.1 Exp. 1 – The system’s frequency response

In order to measure the system’s frequency response, the microphone was positioned directly in front of the system`s speaker at 0.5m. The Smart Microphone gain was configured to 4 v/v (12dB) in order to get the maximum resolution of the ADC and the microphone threshold detection was set to 50%. A linear chirp signal was generated from the systems DSP MCU memory ranging from 1kHz to 100kHz and back to 1 kHz with a trapezoid windowing for the 5% of the signal. The generated chirp to the speaker and the received signal from the microphones were recorded by the Saleae logic analyzer. The experiment was conducted once with the analog HPF module of the microphone enabled and once with the HPF disabled (Figure 20).

In order to retrieve the system’s frequency response, the signals from the microphone and the generated signal to the speaker were aligned by compensating for the time delay generated by the signal’s propagation in air, between the speaker and the microphone. The time delay was retrieved using a synchronization pulse generated in the beginning of the chirp, and by cross correlating this pulse with the received pulse. The system’s frequency response was estimated using “tfestimate” function in Matlab on the aligned data set.

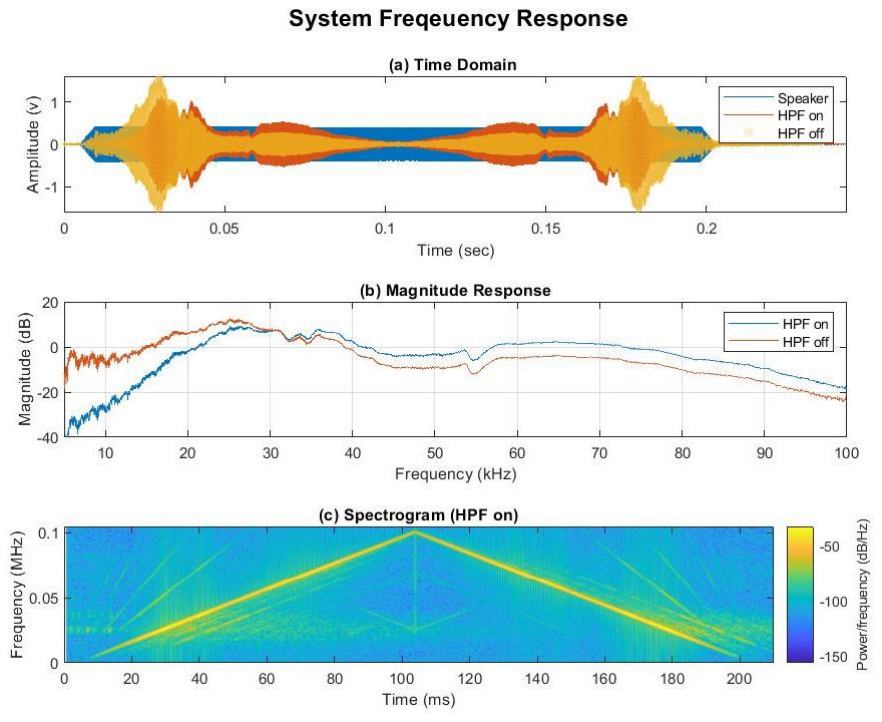
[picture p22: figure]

Figure 20. System’s frequency response, microphone switch and speaker: (a) Frequency response in time domain, (b) Magnitude response of the system, (c) Spectrogram showing that the system has some harmonic distortions (frequencies at double and higher than the main frequency but at a much lower density), In addition it has an echo signal, probably derived from a close by wall, since the echoes have the same delay on the rising side of the chirp and the decreasing side.

The results reveal that the implemented analog high pass filter module significantly improves the frequency response for the 25kHz – 50kHz range, while filtering out the frequencies lower than 20kHz. In addition, from frequency response curve it is noted that the HPF module adds approximately 6dB gain corresponding to the design parameters of the module as a second order high pass filter at a cutoff frequency of 48kHz with a damping factor of 0.5.

## 2.2 Exp. 2 – The switch pass-through mode

The simplest operation mode for the DSP MCU is passing the signal from its input to its output without any modifications to the signal and with minimum latency. The setup used for this experiment is the same as in the frequency response experiment.

Figure 21 presents the recorded signals for the pass-through mode, the output has a barely noticeable delay compared to the input, at the order of 1uS. The delay is generated by the analog characteristics of the microcontrollers ADC / DAC. Corresponding to its frequency response of up to 1Mhz.

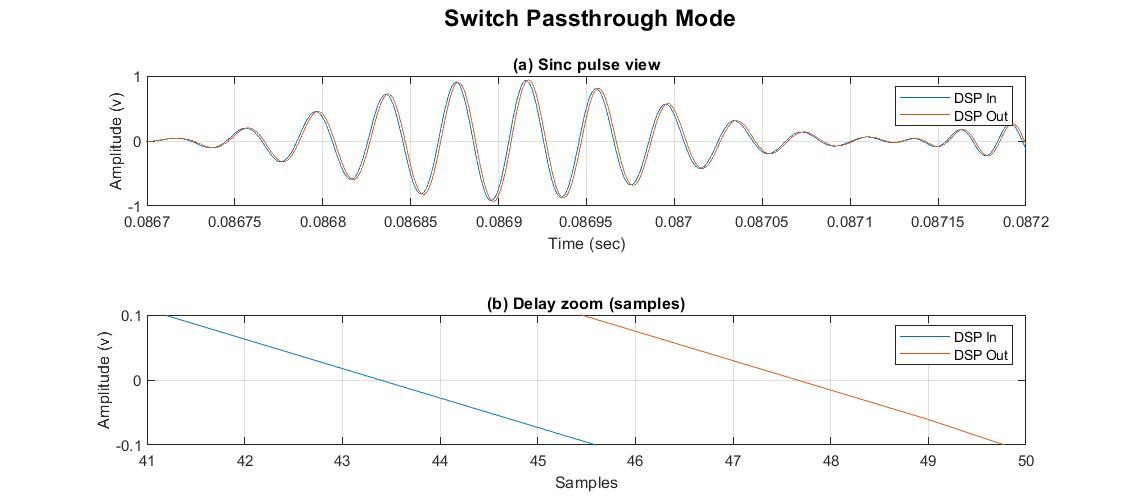
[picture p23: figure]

Figure 21. Switch Pass-through Mode Experiment: (a) Sinc pulse, demonstrates that the generated signal is the same as the input signal. (b) Delay zoom, shows the induced latency, which is accumulated to 4 samples of the Saleae logic analyzer which is set to 3.15 MHz sample rate. And correspond to an order of 1uS latency for the system.

## 2.3 Exp. 3 – Generating delays

In order to simulate an object at various distances for the same setup position an optional software delay to the acoustic signal was implemented using the microphone’s MCU. For a bat such a delay would be equivalent to moving the object backwards. The maximal delay depends on the memory size of the MCU, for the STM32F303 the memory limit is at about 3ms. To demonstrate this capability, both Smart microphone modules were recorded using the setup shown in Figure 18. The Smart Microphone gain was configured to 2 v/v (6dB), the HPF module was set to on and the microphone threshold detection set to 50%. The acoustic signal was generated by the Chirp Box. The signal was a recorded signal of an actual bat call, as recorded by a GRAS microphone (PD40, GRAS). Both microphones are recorded simultaneously while each has a different delay setting.

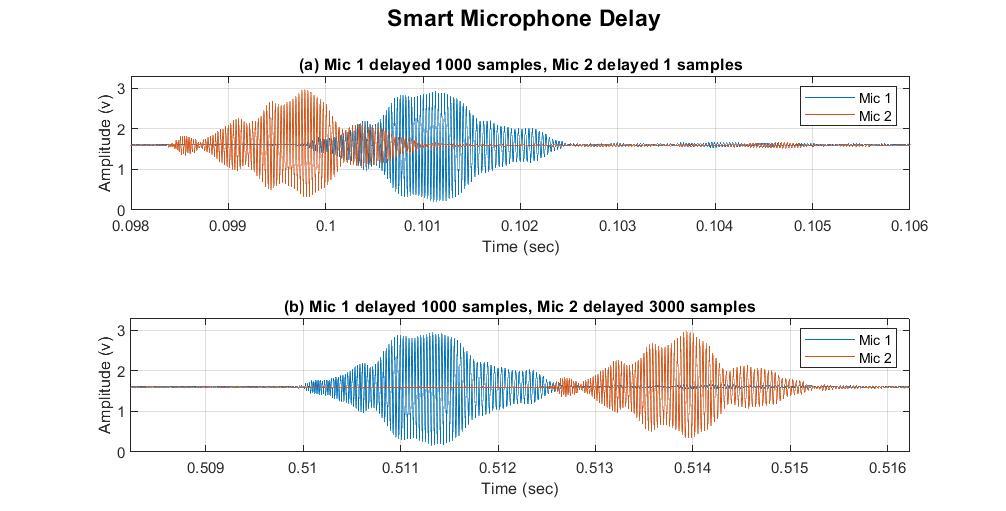
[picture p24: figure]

Figure 22. Smart Microphone delay experiments: (a) Mic 1 Delayed, (b) Mic 2 Delayed. The plots demonstrate the influence of the software delay induced for each microphone and how one signal can be delay compared to the other with the appropriate settings described in the titles for the graphs.

An additional use for the delay feature is to delay the acoustic signal generated by the microphone while the Switch MCU switches between the microphone sources, allowing fluent transition between sources. This is accomplished since the Smart microphone that generates a trigger when a signal is present, but the trigger is generated only after the signal level passes a pre-defined threshold those missing a fraction of the beginning of the signal. By delaying the signal, with an appropriate amount. The trigger will be generated before the actual acoustic signal has reached the Switch.

## 2.4 Exp. 4 – Testing the switch filter mode

To test the bats’ perception and response to various effects, it is required to implement real time signal processing’s to the signal. One of the most basic implementations is a standard digital filter. In this experiment the performance of a high pass filter was evaluated. For optimized computational power the filter is implemented as an infinite impulse response filter (IIR) using the direct form 1 configuration. Several Butterworth high pass filters were tested at various orders.

The Switch filter mode is implemented on the DSP MCU. In this mode the MCU performs a high pass filter using the configured coefficients and the defined order by the Matlab GUI. The MCU samples the signal using an analog to digital converter (ADC) at 12bit resolution, applies the predefined filter and adds a digital gain afterwards it outputs the signal using embedded hardware digital to analog converter (DAC) of the microcontroller at a resolution of 12 bits. The setup used for this experiment is the same as in the system frequency response experiment. Figure 23 presents two recordings of the HPF filter mode. One for an HPF at 50kHz with 2 order, and the other is a 50kHz with 8 order.

Figure 23. Switch High Pass Filter Mode: (a) HPF 2 order filter, (b) HPF 8 order filter, (c) Filter estimation. The figure demonstrates the estimated frequency response for the implemented filters derived from the recorded data, using the “tfestimate” function in Matlab and they correlate to the implanted filters for the DSP MCU.

In addition to evaluating the filter implementation the filter computation load was also tested. The sampling frequency of the setup is directly influenced by the number of calculations implemented at every operating mode and since implementing high order filters requires more operations to implement the sampling frequency decreases for higher filter orders, the values are summed up in Table 1..

Filter order | Sampling frequency (kHz)
2 | 1135
4 | 885
6 | 725
8 | 614
10 | 533
Table 1. Filter order vs Sampling frequency for Filter Mode experiment: The higher the filter order the lower the sampling frequency.

## 2.5 Exp. 5 – Testing the trigger HPF mode

One of the most difficult issues with the playback system is the direct feedback from the speakers to the microphones. Since the system transmits the acoustic signals received by the microphone in real time, a positive feedback loop may occur, resulting in self-resonance at the resonance frequencies of the system. From the frequency response of the system and actual resonance experiments those frequencies are at the range of 25kHz-35kHz. Depending on the speaker angle and the microphone filter implementation.

In order to overcome this challenge a trigger mode has been implemented. The trigger mode acts as a simple signal presence detector based on a threshold detection and it silences the system after the signal has been received and transmitted using a countdown technique – after a signal presence is detected a countdown is initiated and sets the number of samples to be passed before the system silences the channel. The number of samples to be transmitted after a signal is detected is set by the Trigg pass value. After the countdown is completed a silencing period is implemented at the length of the ‘Trig pause’ value. The silencing effect causes any residue acoustic signals to dissipate and reduces the chances for the system resonating. In addition to the trigger detection, this mode implements an HPF using the same coefficients used in the HPF mode.

In order to test the performance of this mode the speaker was positioned directly in front of the microphone (Figure 18) which is the worst configuration possible because the microphone picks up any emission from the speaker. Bat sound signals were generated by the chirper box, and the signals recorded by the Saleae logic. The results are seen in Figure 24. The top plot demonstrates how the system enters self-resonance just from background noise even with a short silencing period of 10ms, the middle plot demonstrates how extending the silencing period to 20ms fixes this issue. In the bottom plot it is possible to see how the system starts resonating from a direct feedback loop.

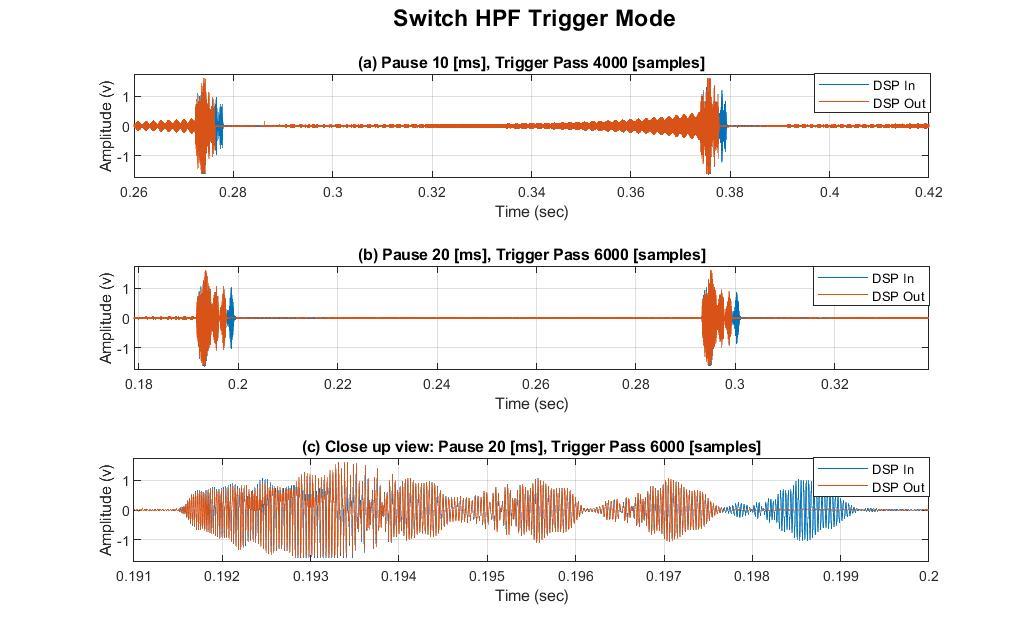
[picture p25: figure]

Figure 24. Switch HPF Trigger Mode, Resonance handling: (a) HPF Trigger mode with the ms pause and 4000 samples to pass, notable the self-resonance generated by background noise. (b) HPF Trigger mode with 20 ms pause and 6000 samples to pass, the self-resonance is disabled. (c) Zoom on the signal of HPF Trigger mode with 20 ms pause and 6000 samples pass. The repetitive pulse length directly correlated to the distance from the speaker to the microphone. Which is approximately 0.5m, and the repetitive pulse is approximately 1.5ms which is at the speed of sound of 343m/s covers 0.51m. In addition, the figure demonstrates the trig pass implementation and that the microphone has recorded the last generated pulse after the system has been silenced – I.e. the signal that has covered the distance between the speaker and the microphone.

## 2.6 Exp. 6 – Trigger mode gain adjustments

In order to simulated variable echo gains which in nature can be generated by the flapping wings of a butterfly. The Trigger mode gains was implemented. The Trigger mode gains is an extension mode to the Trigger mode, in addition to the implemented in the Trigger mode, this mode adds a variable gain to the detected signals. The gains are set by a predefined value and switched after each detected signal. The results are seen in Figure 25.

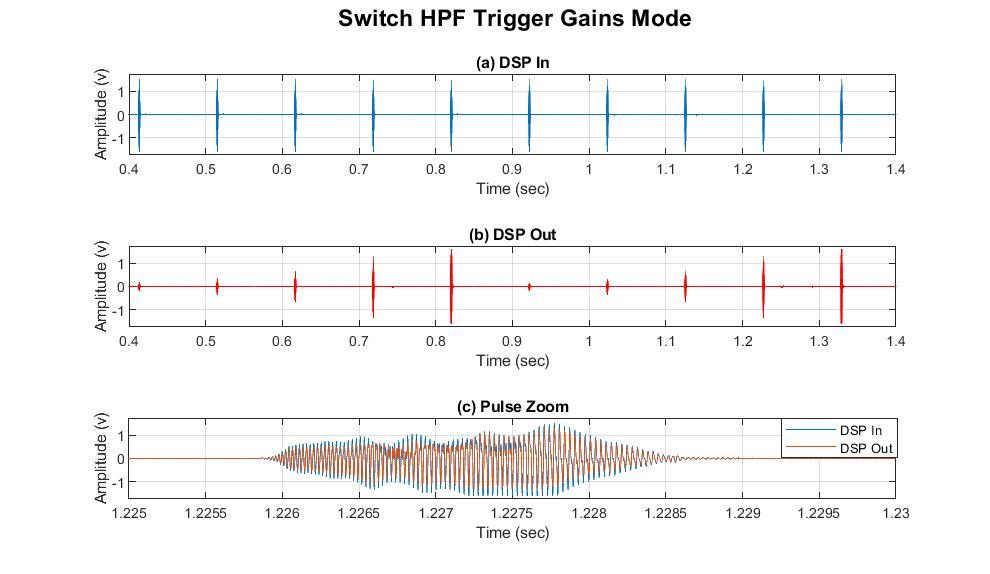
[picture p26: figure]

Figure 25. Switch HPF Trigger Gains Mode: (a) DSP in Signal, (b) DSP Out signal -notable the variable gains for the pulses recorded at (a) , (c) Zoom on a single pulse with a slightly lower gain.

## 2.7 Exp. 7 – Auto mode

One of the most innovative features of the system is the ability to redirect sound from various channels to several speakers in real time and automatically. This capability can be used to generate obstacles near the bat by detecting the closest source to the bat. In addition, this mode can be used to generate a virtual predator by generating a “chasing” effect.

To demonstrate this capability, the Auto Mode was implemented and tested using the experiment setup 2 described in Figure 18, The Chirper box was moved in front of a microphone array to a distance of 1 meter, playing a prerecorded bat call stored in its memory and at a repetition of 10 pulses per second. The received signals from each microphone were logged by a Saleae logic including the trigger pulses. The results of the experiment are demonstrated in Figure 26. The figure shows how the system switches automatically from the nearest microphone and generates a sound wave in real time.

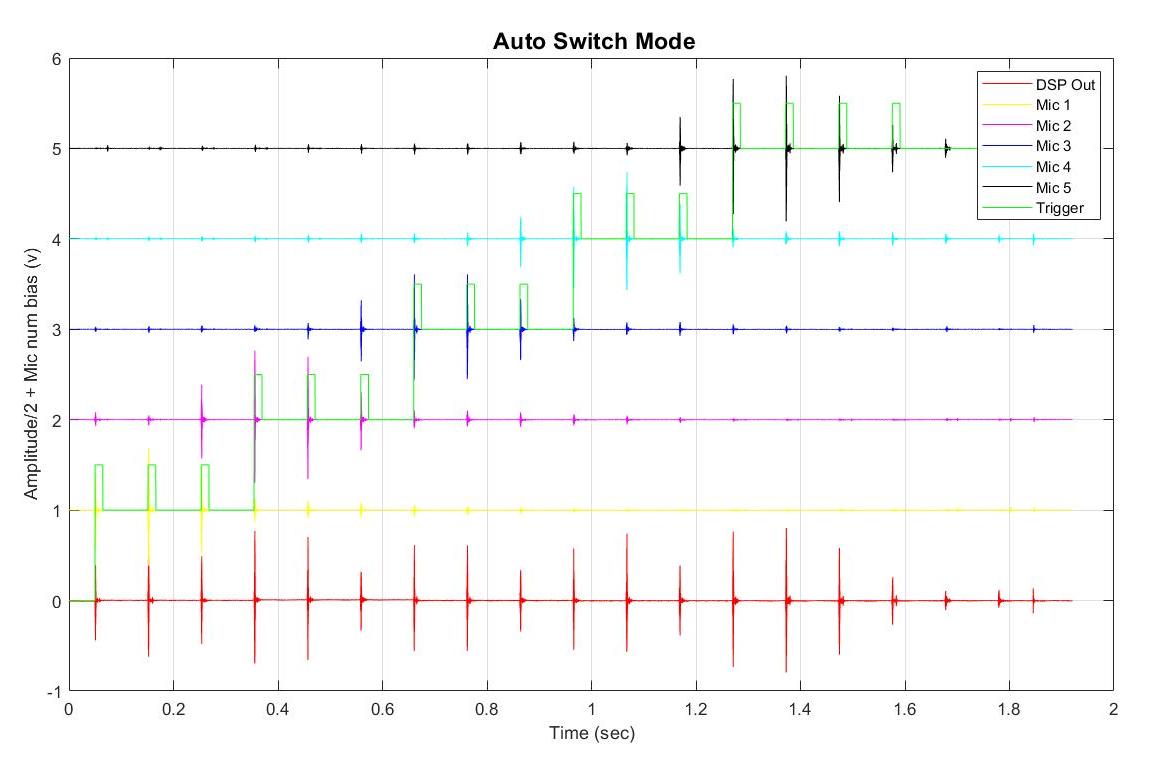
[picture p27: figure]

Figure 26. Auto switch mode: the plot demonstrates the signals for each microphone, the generated signal and the trigger pulse generated by the microphone corresponding to the microphone number as logged by the Switch GUI. Each trigger the signal is rerouted from the triggered microphone to a corresponding speaker.

The ability to switch between microphones in real time is mainly achieved by the system’s architecture. Each of the microphones contains its own microprocessor which is responsible for its own signal detection. When a microphone detects a signal, it generates a trigger which the Switch MCU receives and processes. Since a trigger is a simplified representation of a signal presence the workload for the Switch MCU is very low and it can handle multiple microphones simultaneously. The generated pulses are recorded by the Switch Matlab GUI and presented in Table 2.

Trigger | Mic | Time (sec)
1 | 1 | 379.71
2 | 1 | 379.813
3 | 1 | 379.916
4 | 2 | 380.019
5 | 2 | 380.122
6 | 2 | 380.226
7 | 3 | 380.329
8 | 3 | 380.432
9 | 3 | 380.535
10 | 4 | 380.639
11 | 4 | 380.742
12 | 4 | 380.845
13 | 5 | 380.948
14 | 5 | 381.051
15 | 5 | 381.155
16 | 5 | 381.258
17 | 5 | 381.465
18 | 5 | 381.532
Table 2 Generated table by the Switch GUI: Records the Trigger number, Trigger source and time stamp of the trigger.

## 3 Future directions

Although the system has been developed extensively tested thoroughly and implemented in actual experiments, a lot of improvements are still optional, which can induce interesting experiments and demonstration.

- Upgrade to Differential signaling – The use of a differential signaling can significantly improve noise rejection in the wiring between modules as opposed to the single ended implementation.
- Applying an improved external signal recording oscilloscope for a better resolution ADC
- Upgrading the DSP MCU to a better ADC resolution and higher performance such as the NUCLEO-H743ZI which has 2.5 the current DSP performance, and able to run at 480 MHz, with better ADC. The new version MCU also incorporates a high-speed USB at 480 Mbit, which can allow real time recordings of several microphone signals.
- Upgrading Smart Microphone MCU to a newer better version such as the NUCLEO-G431KB which has 2.5 the current MCU performance, and able to run at 170 MHz, with hardware IIR filtering which can offload some of the MCU work load.
- Adding a PGA module to the output signal will allow better analog performance to the generated signals.
- General improvements to the software.
- Adding real time signal triangulation for position estimation and enabling position-based interactions.
- Adding an optional DMA mode. Although using a DMA implements some delay to the signal, the use will allow better ADC DAC timings and release resources for more complex signal processing.
- Adding an analog switch for the Smart Microphone module to switch between signal sources – analog signal from microphone or the generated signals from the MCU DAC.
- Implementing better signal detection – based on bandpass filtering or cross correlation to prerecorded signals.

## 4 Appendix A

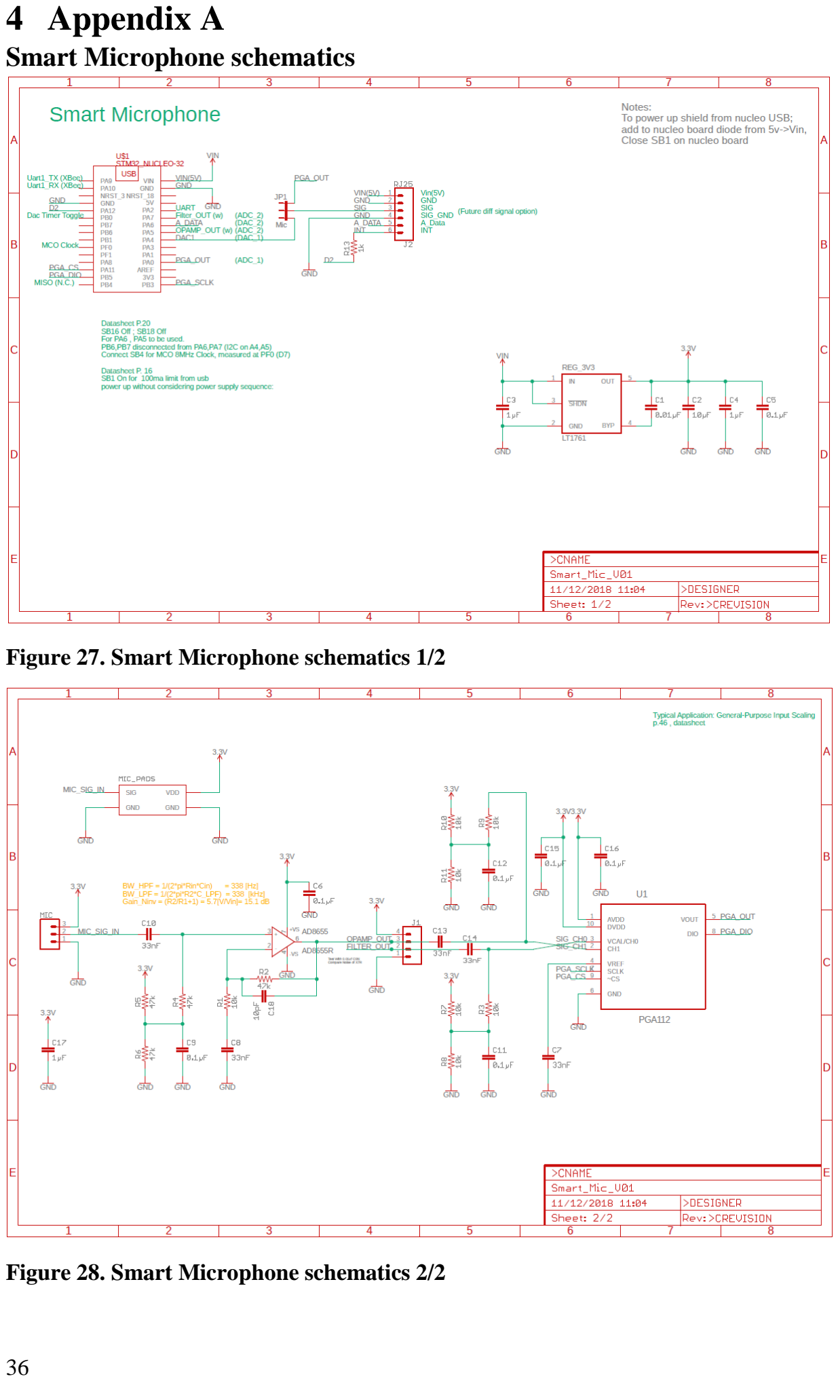
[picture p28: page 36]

Smart Microphone schematics

Figure 27. Smart Microphone schematics 1/2

Figure 28. Smart Microphone schematics 2/2

Figure 29. HPF Module

Figure 30. HPF Module simulation

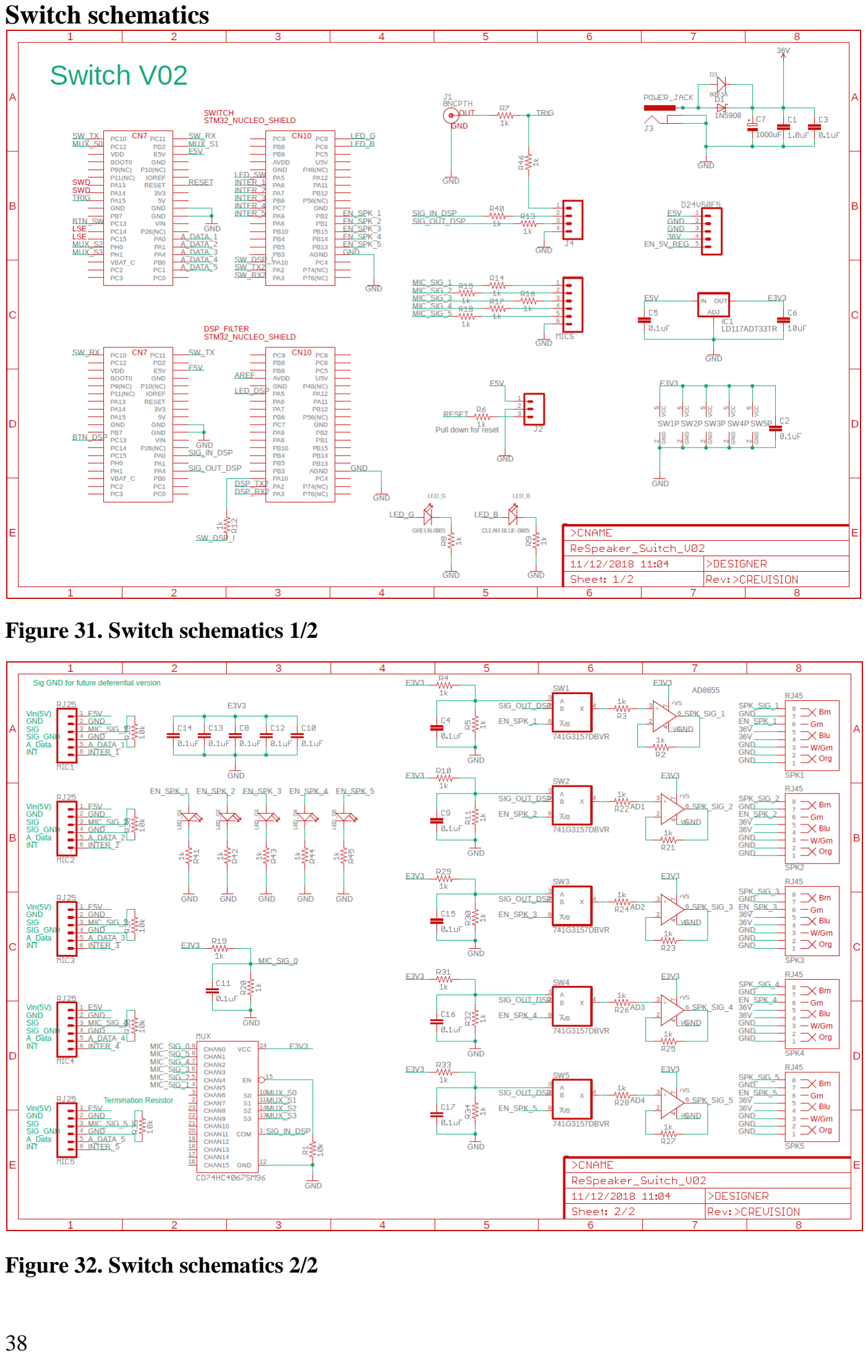
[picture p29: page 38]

Switch schematics

Figure 31. Switch schematics 1/2

Figure 32. Switch schematics 2/2

Speaker amplifier schematics

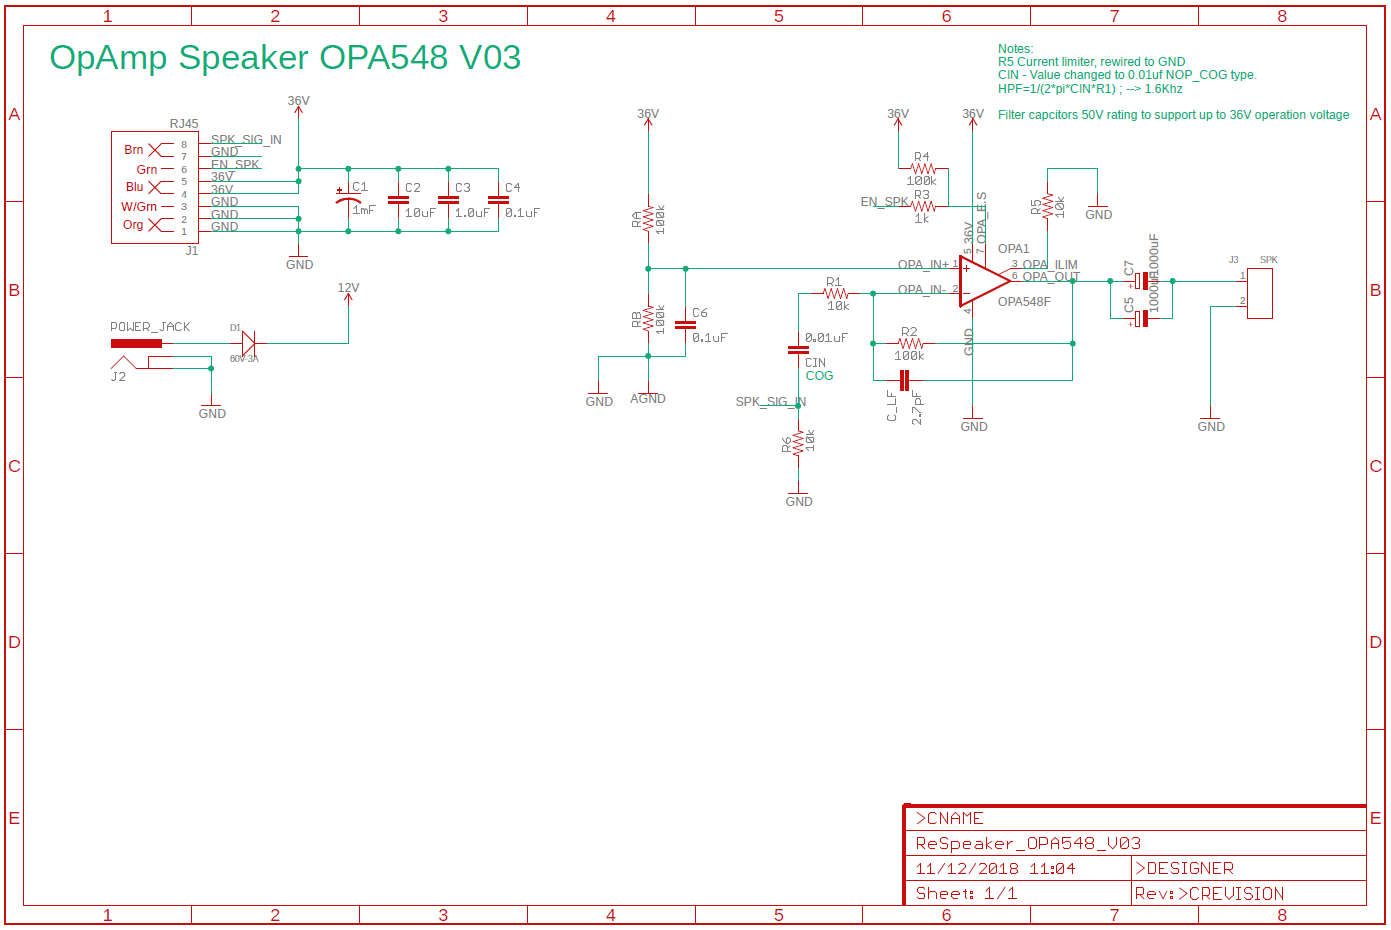
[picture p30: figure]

Figure 33. Speaker amplifier schematics

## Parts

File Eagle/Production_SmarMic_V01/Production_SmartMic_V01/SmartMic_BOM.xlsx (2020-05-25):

Qty | Value | Digikey | Device | Package | Parts | Description | Column1 | _1
1 |  |  | CONN_03 | 1X03 | MIC | Multi connection point. Often used as Generic Header-pin footprint for 0.1 inch spaced/style header connections
1 |  |  | CONN_04 | 1X04 | J1 | Multi connection point. Often used as Generic Header-pin footprint for 0.1 inch spaced/style header connections
2 | 0.1uF |  | 1.0UF-0805-25V-10% | 0805 | C27, C31 | 1µF ceramic capacitors
7 | 0.1µF |  | 0.33UF/330NF-0805-50V-10% | 0805 | C5, C6, C9, C11, C12, C15, C16 | 0.33µF/330nF ceramic capacitors
2 | 0.8 |  | SPU0410LR5H-QBSPU0410LR5H-QB_0.8 | SPU0410LR5H-QB_0.8 | _MIC_1, _MIC_4
1 | 1.0uF |  | 1.0UF-0805-25V-10% | 0805 | C26 | 1µF ceramic capacitors
13 | 10k |  | RESISTOR0805 | 0805 | R1, R3, R7, R8, R9, R10, R11, R19, R20, R21, R22, R23, R24 | Generic Resistor Package
1 | 10pF |  | 0.33UF/330NF-0805-50V-10% | 0805 | C18 | 0.33µF/330nF ceramic capacitors
1 | 10µF |  | 0.33UF/330NF-0805-50V-10% | 0805 | C2 | 0.33µF/330nF ceramic capacitors
1 | 1k |  | RESISTOR0805 | 0805 | R13 | Generic Resistor Package
3 | 1µF |  | 0.33UF/330NF-0805-50V-10% | 0805 | C3, C4, C17 | 0.33µF/330nF ceramic capacitors
1 | 30pF |  | 1.0UF-0805-25V-10% | 0805 | C32 | 1µF ceramic capacitors
2 | 330pF |  | 1.0UF-0805-25V-10% | 0805 | C28, C29 | 1µF ceramic capacitors
6 | 33nF |  | 0.33UF/330NF-0805-50V-10% | 0805 | C1, C7, C8, C10, C13, C14 | 0.33µF/330nF ceramic capacitors
3 | 33nF |  | 1.0UF-0805-25V-10% | 0805 | C30, C34, C37 | 1µF ceramic capacitors
4 | 47k |  | RESISTOR0805 | 0805 | R2, R4, R5, R6 | Generic Resistor Package
2 | AD8655R |  | AD8655R | SO8 | AD8655, HPF_V02 | Low Noise, Precision CMOS Amplifier
1 | Con |  | CONN_04 | 1X04 | J4 | Multi connection point. Often used as Generic Header-pin footprint for 0.1 inch spaced/style header connections
1 | LT1761 | ‎LT1761IS5-3.3#TRMPBFCT-ND‎ | LT1761 | SOT23-5 | REG_3V3 | Regulator
1 | MIC_PADS | ‎423-1139-1-ND | MIC_PADS | MIC_PADS | U$2
1 | Mic_Sig |  | CONN_02 | 1X02 | J14 | Multi connection point. Often used as Generic Header-pin footprint for 0.1 inch spaced/style header connections
1 | Mic_Sig |  | CONN_021X02_2MM | 1X02_2.0MM | J8 | Multi connection point. Often used as Generic Header-pin footprint for 0.1 inch spaced/style header connections
1 | Mic_Supply |  | CONN_02 | 1X02 | J13 | Multi connection point. Often used as Generic Header-pin footprint for 0.1 inch spaced/style header connections
1 | Mic_Supply |  | CONN_021X02_2MM | 1X02_2.0MM | J7 | Multi connection point. Often used as Generic Header-pin footprint for 0.1 inch spaced/style header connections
1 | PGA112 |  | PGA113AIDGST | SOP50P490X110-10N | U1 | PROGRAMMABLE GAIN AMPLIFIER with MUX
1 | RJ25 | ‎A31417-ND‎ | RJ11-6 | RJ11-6 | J2 | RJ11 Jack - 6 pin
1 | STM32_NUCLEO-32 | ‎497-15981-ND‎ | STM32_NUCLEO-32 | STM32_NUCLEO-32 | U$1 | STM32_NUCLEO-32
1 | Mic |  | JUMPER-3PTH | 1X03 | JP1

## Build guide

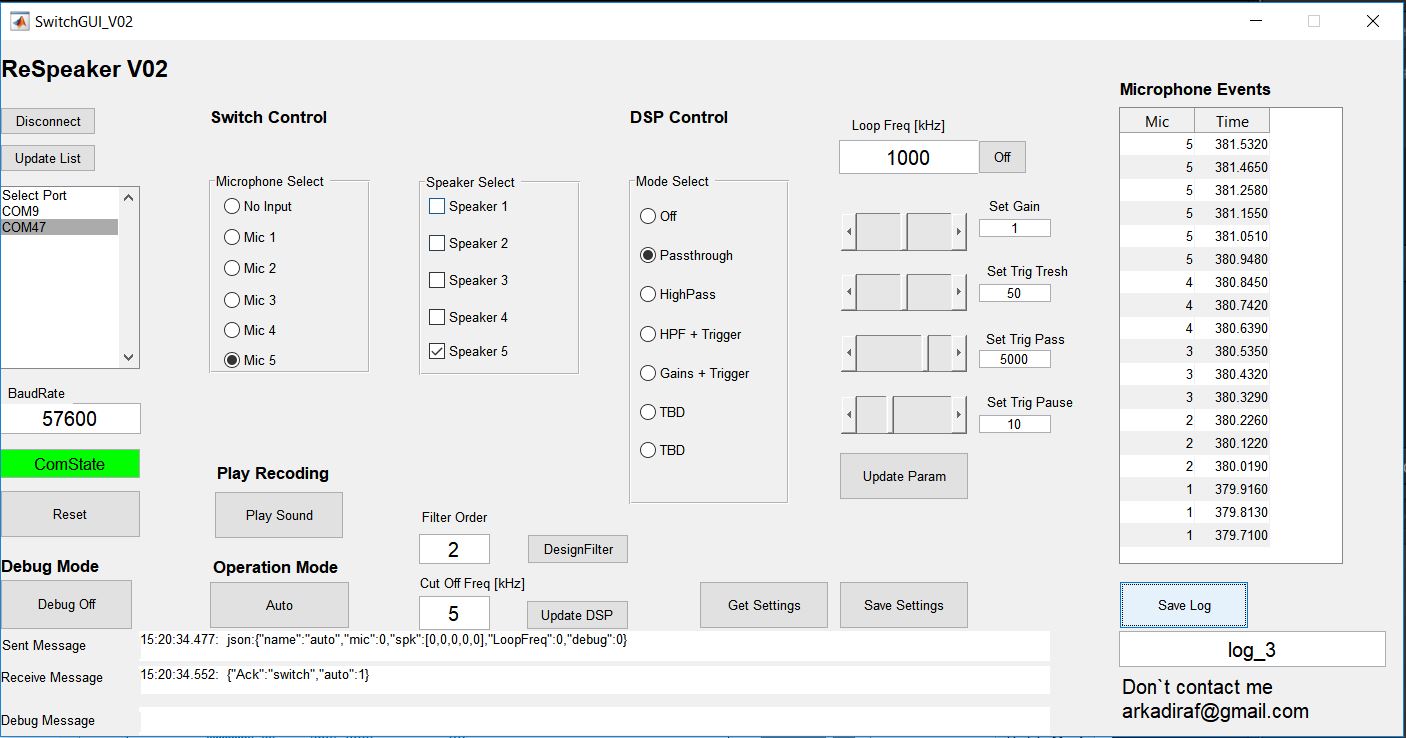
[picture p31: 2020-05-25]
SystemTestExperiments/Mode_Auto_29_07_2019/SwitchSetup_Log3.JPG

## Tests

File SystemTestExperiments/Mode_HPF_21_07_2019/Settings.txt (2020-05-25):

Mic Speaker distance 0.9m
Mic gain 1, mic thresh 50%
Mic FilterOff

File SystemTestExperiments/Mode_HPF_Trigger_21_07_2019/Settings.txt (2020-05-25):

Mic Speaker distance 0.9m
SpeakerSystem distance 0.5m
Mic gain 2, mic thresh 50%
Mic FilterOn
Switch Freq 1040 kHz
TrigPass_4000
Pause_10
HPF 2_5kHz

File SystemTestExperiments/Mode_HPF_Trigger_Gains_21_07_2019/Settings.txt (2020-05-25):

Mic Speaker distance 0.9m
SpeakerSystem distance 0.5m
Mic gain 2, mic thresh 50%
Mic FilterOn
Switch Freq 786 kHz
TrigPass_4000
Pause_20 ms
HPF 2_5kHz

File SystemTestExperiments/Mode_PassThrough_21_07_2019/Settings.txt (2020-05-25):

Mic Speaker distance 0.9m
Mic gain 1, mic thresh 50%
Mic FilterOff
Switch Freq 5900 kHz

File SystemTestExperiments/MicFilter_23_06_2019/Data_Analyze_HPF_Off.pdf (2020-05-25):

%%%%%%%%%%%%%%%%%%%%%%%%%%%%%%%%%%%%%%%%%%%%%%%%%%%%%
% Analyze sample data - 24/06/2019 | %
% Arkadi Rafalovich - % Arkadiraf@gmail.com | %
%%%%%%%%%%%%%%%%%%%%%%%%%%%%%%%%%%%%%%%%%%%%%%%%%%%%% clc
clear

% Setup description
%{
Mic Speaker distance 0.5m
Supply voltage to Speaker 12V
Mic gain 4, mic thresh 50%
Scan 1-100 khz HPF Filter Board at 48Khz, xi 0.5 second order Op-Amp Speaker Gain is set to 1 (no gain, verified with scope) Test with Vifa speaker.
Test with SMD microphone

Data:
analog_channel_0 - Mic Select analog_channel_1 - Output Signal %}

### Open Data

%Open Recording
load HPF_Off.mat
%Open Recording
%load HPF_On.mat

%open position selected data load PosSig.mat

### Variables

%time vector for plots
time_vector = ((1:1:size(analog_channel_0,1))/analog_sample_rate_hz)';

%sample time
Ts = 1/analog_sample_rate_hz;

% Remove Bias from signals
micSignal | = | analog_channel_0-mean(analog_channel_0);
outputSignal | = | analog_channel_1-mean(analog_channel_1);

### Select Position Signal

% PosSig = outputSignal(361800:(364600-1)); % use only the 25khz signal
% PosSig = outputSignal(361800:(363072-1)); % save PosSig PosSig
% plot(outputSignal)
% [x]=ginput(2)
% PosSig=micSignal(x(1):x(2))

### Recorded signals

figure(1); % time response

subplot(2,1,1)
plot(time_vector,outputSignal) title('Output');
axis tight
xlabel('[sec]');
ylabel('[volt]');

subplot(2,1,2)
plot(time_vector,micSignal) title('Mic');
axis tight
xlabel('[sec]');
ylabel('[volt]');

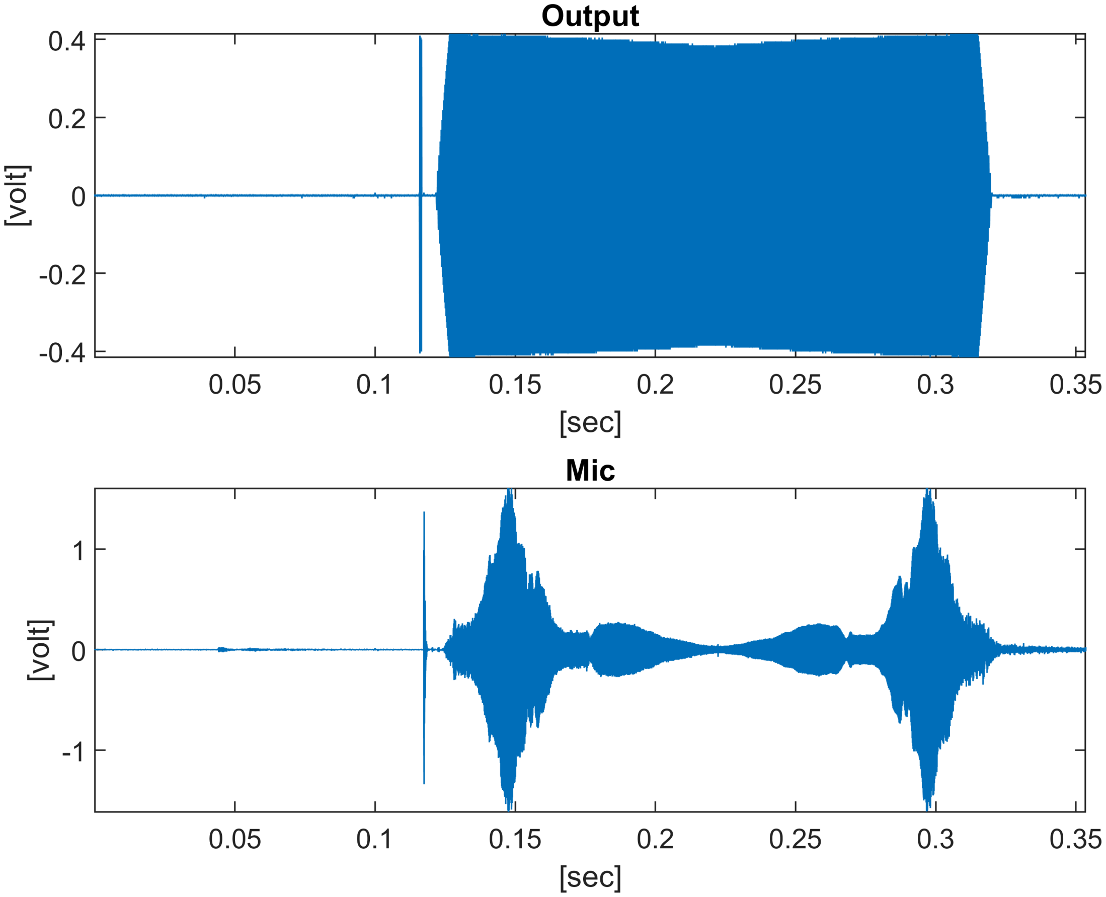
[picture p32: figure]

### Find Signal Delay

% Variables
signalCrossingValue = 0.5; % percentage of the max value from the signal numSamplesBeforeIndex = 1000; % number of samples used before crossing index
numSamplesAfterIndex = 2500; % number of samples used after crossing index
% filter signal before looking for the delay
bpFilt = designfilt('bandpassiir', 'FilterOrder', 20, 'HalfPowerFrequency1', 20000, 'HalfPowerFrequency2', 60000, 'SampleRate', analog_sample_rate_hz); %fvtool(bpFilt) % visualize filter response

% apply filter
outputSignalFiltered = filter(bpFilt,outputSignal);
micSignalFiltered = filter(bpFilt,micSignal);
% find position signal
outputSignal_Index = find(outputSignalFiltered > max(outputSignalFiltered)*signalCrossingValue,1,'first'); micSignal_Index = find(micSignalFiltered > max(micSignalFiltered)*signalCrossingValue,1,'first');
% generate array for cross correlation
outputSignalPos = outputSignal(outputSignal_Index - numSamplesBeforeIndex : outputSignal_Index + numSamplesAfterIndex); micSignalPos = micSignal(micSignal_Index - numSamplesBeforeIndex : micSignal_Index + numSamplesAfterIndex);
% find signal delay
delayOutput = finddelay(PosSig,outputSignalPos) + outputSignal_Index - numSamplesBeforeIndex;
delayMic = finddelay(PosSig,micSignalPos) + micSignal_Index - numSamplesBeforeIndex;

% generate signal to mark the delay
markDelay = [zeros(delayOutput,1) ; ones(delayMic-delayOutput,1) ; zeros(size(micSignal,1)-delayMic,1)];

figure(3); % Signal delay
plot(time_vector,outputSignal)
hold on
plot(time_vector,micSignal) plot(time_vector,markDelay) hold off
title('Signal');
axis tight
xlabel('[sec]');
ylabel('[volt]');

% adjust signals
micSignalAdjusted = [micSignal(delayMic-delayOutput : end) ; zeros(delayMic-delayOutput-1,1)];

% Select signals sweep
micSignalSweep = micSignalAdjusted(delayOutput + numSamplesAfterIndex + numSamplesBeforeIndex : end); outputSignalSweep = outputSignal(delayOutput + numSamplesAfterIndex + numSamplesBeforeIndex : end); timeVectorSweep = time_vector(delayOutput + numSamplesAfterIndex + numSamplesBeforeIndex : end);

figure(4); % signals delayed
plot(time_vector,outputSignal)
hold on
plot(time_vector,micSignalAdjusted) hold off
title('Signal');
axis tight
xlabel('[sec]');
ylabel('[volt]');

figure(5); % signals delayed plot(timeVectorSweep,outputSignalSweep) hold on
plot(timeVectorSweep,micSignalSweep) hold off
title('Signal');
axis tight
xlabel('[sec]');
ylabel('[volt]');

### Spectogram

% Spectogram
figure(6);
spectrogram(micSignalSweep,4096,4000,4096,analog_sample_rate_hz,'yaxis'); xlim([0 210]);
ylim([0 0.105]);

### System identification / Bode

% Link https://www.mathworks.com/help/supportpkg/analogdevicesadalm1000/examples/estimate-the-transfer-function-of-a-circuit-using-live-measurements.html % estimate bode
[TFxy,Freq] = tfestimate(outputSignalSweep, micSignalSweep,[],[],[],analog_sample_rate_hz);
%[TFxy,Freq] = tfestimate(micSignalSweep,outputSignalSweep,[],[],[],analog_sample_rate_hz);
Mag = abs(TFxy);
Phase = - rad2deg(unwrap(angle(TFxy)));
MagdB = 20*log10(Mag);

% plot ranges
sweepStart = 5e3;
sweepEnd = 100e3;

% plot Magnitude
figure(7);
semilogy(Freq,Mag);
xlim([sweepStart sweepEnd]) xlabel('Frequency (Hz)')
ylim([0.01 20])
ylabel('Magnitude')
grid on
legend('Frequency response') title({'Magnitude response'});

% plot magnitude dB
figure(8);
plot(Freq,MagdB);
xlim([sweepStart sweepEnd]) xlabel('Frequency (Hz)')
ylim([-40 20])
ylabel('Magnitude (dB)')
grid on
legend('Frequency response') title({'Magnitude response'});

% Bode Plot
figure(10);

subplot(2,1,1);
plot(Freq,MagdB);
xlim([sweepStart sweepEnd]) xlabel('Frequency (Hz)')
ylim([-40 20])
ylabel('Magnitude (dB)')
grid on
legend('Frequency response')
title({'Magnitude response'});

subplot(2,1,2);
plot(Freq,Phase - Phase(find(Freq > 25e3,1,'first'))) xlim([sweepStart sweepEnd])
xlabel('Frequency (Hz)')
ylabel('Phase (deg)')
grid on
legend('Frequency response') title({'Phase response'});

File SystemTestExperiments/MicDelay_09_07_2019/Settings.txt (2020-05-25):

Mic Speaker distance 0.5m
Mic gain 2, mic thresh 50%
HPF On

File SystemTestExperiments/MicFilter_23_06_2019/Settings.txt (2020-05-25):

Mic Speaker distance 0.5m
Mic gain 4, mic thresh 50%

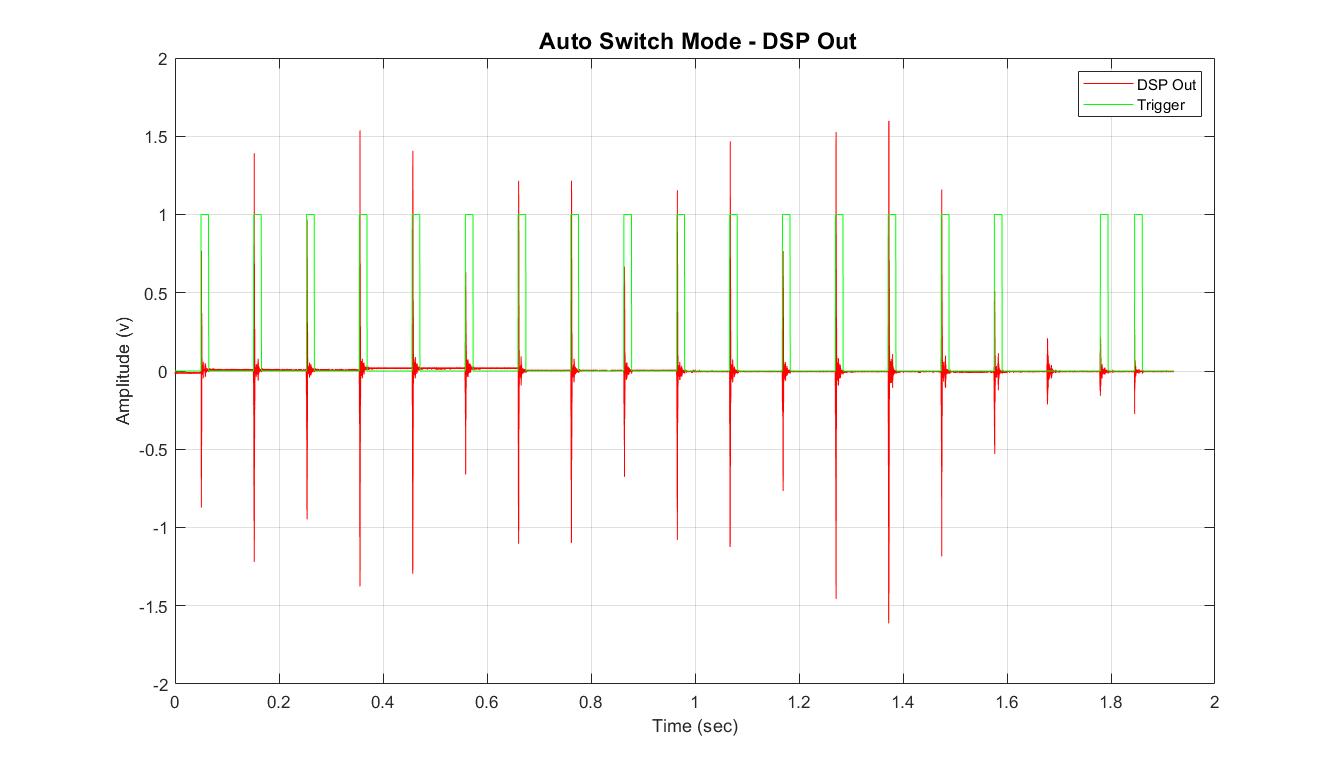
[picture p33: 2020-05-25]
SystemTestExperiments/Mode_Auto_29_07_2019/AutoSwitchMode_Out.jpg

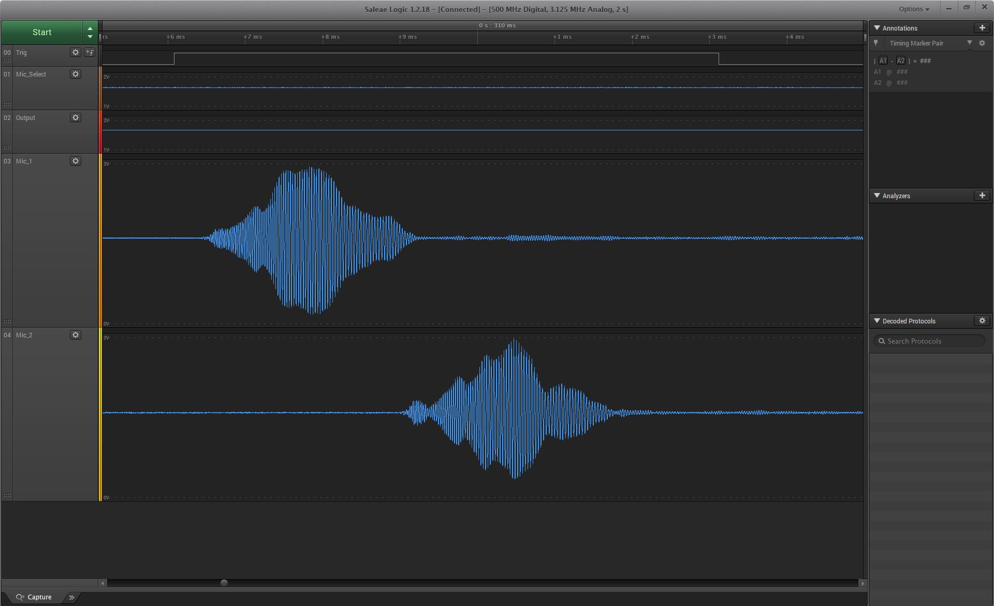
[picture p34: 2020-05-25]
SystemTestExperiments/MicDelay_09_07_2019/MicDelay_1000vs3000.JPG

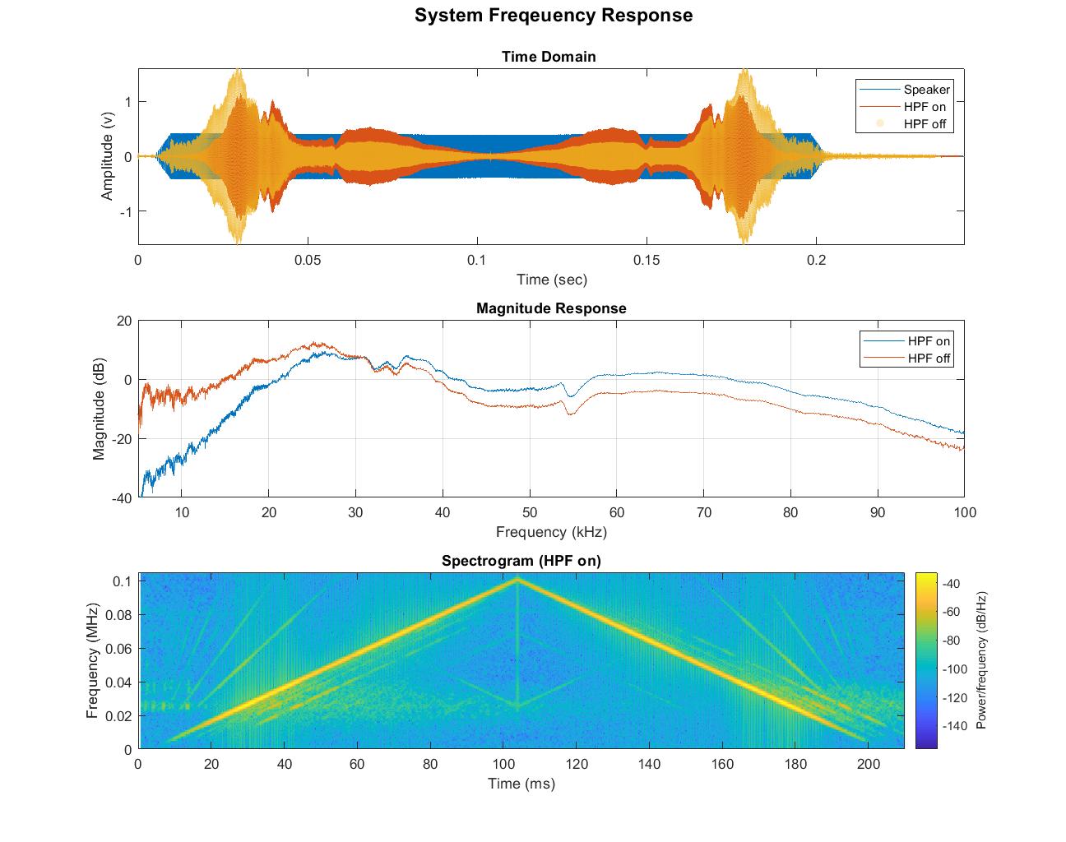
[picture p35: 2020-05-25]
SystemTestExperiments/MicFilter_23_06_2019/FrequencyResponsePlot.jpg

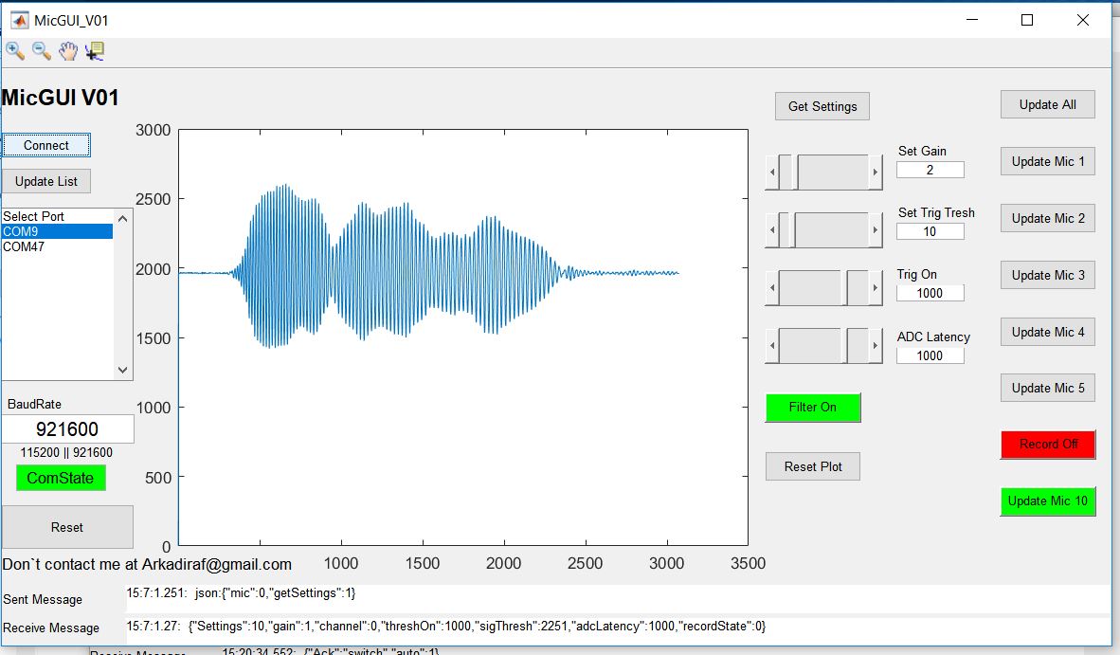
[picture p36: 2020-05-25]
SystemTestExperiments/Mode_Auto_29_07_2019/MicSettings.JPG

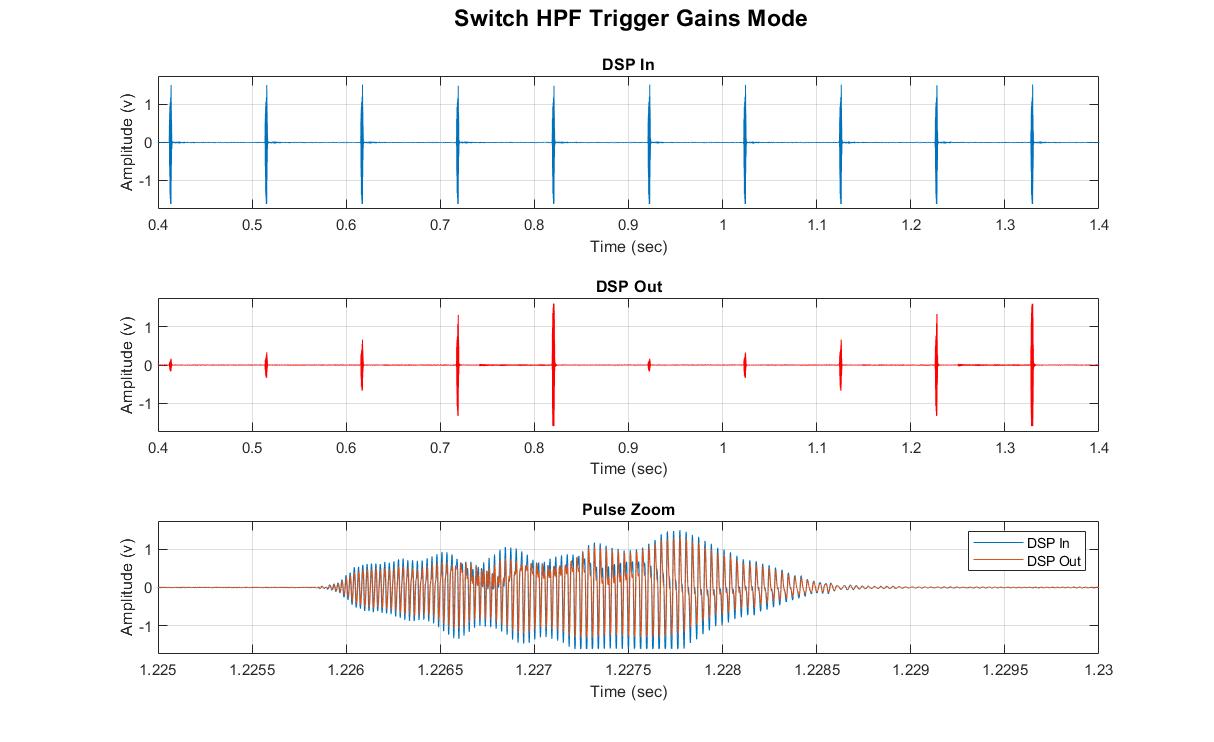
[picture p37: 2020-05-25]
SystemTestExperiments/Mode_HPF_Trigger_Gains_21_07_2019/ModeHPF_Trig_Gains.jpg

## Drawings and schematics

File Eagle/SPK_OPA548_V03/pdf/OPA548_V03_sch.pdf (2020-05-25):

A

A

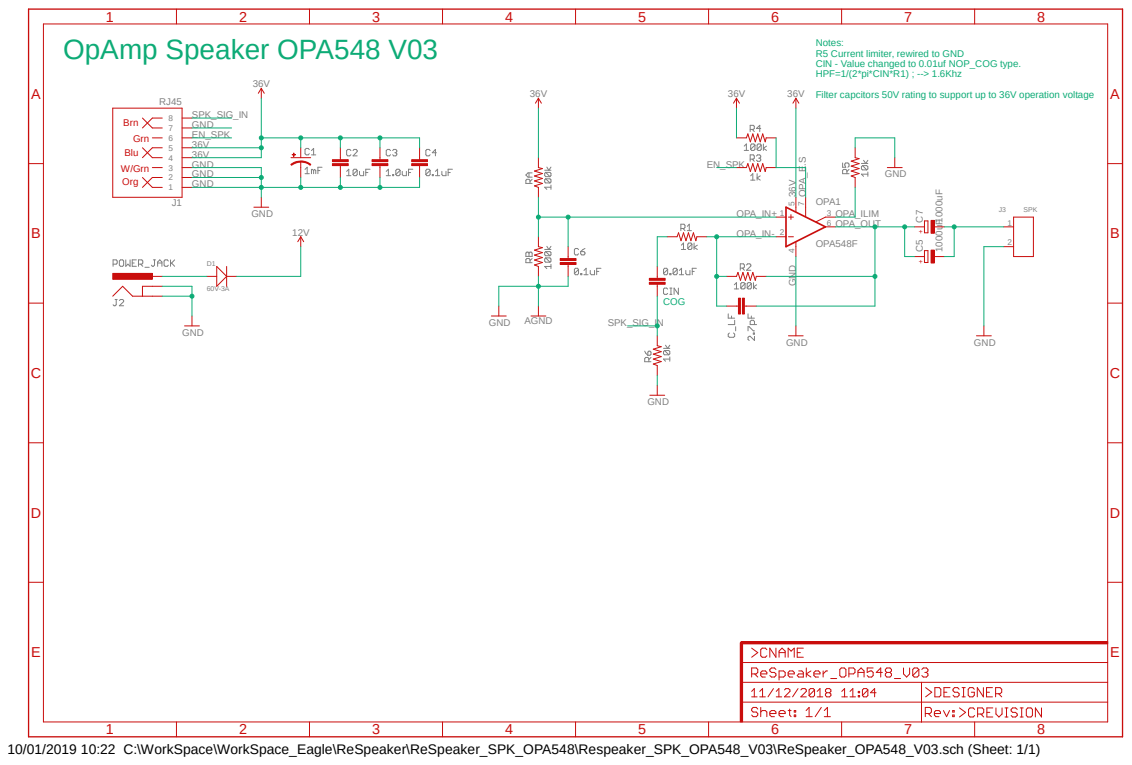
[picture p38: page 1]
OPA548F; GND; AGND; OPA1; OPA_IN+; OPA_IN-; OPA_E.S; OPA_ILIM OPA_OUT; SPK_SIG_IN; EN_SPK; 36VGND; Org; Blu; Brn; W/Grn; Grn; COG; OpAmp Speaker OPA548 V03

Notes:
R5 Current limiter, rewired to GND
CIN - Value changed to 0.01uf NOP_COG type.
HPF=1/(2*pi*CIN*R1) ; --> 1.6Khz
Filter capcitors 50V rating to support up to 36V operation voltage
SPK GND

10/01/2019 10:22 C:\WorkSpace\WorkSpace_Eagle\ReSpeaker\ReSpeaker_SPK_OPA548\Respeaker_SPK_OPA548_V03\ReSpeaker_OPA548_V03.sch (Sheet: 1/1)

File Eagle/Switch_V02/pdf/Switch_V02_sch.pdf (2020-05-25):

# D1 2 5 GND VCC SW1P 2 5 GND VCC SW2P 2 5 GND VCC SW3P 2 5 GND VCC SW4P 2 5 GND VCC SW5P

A

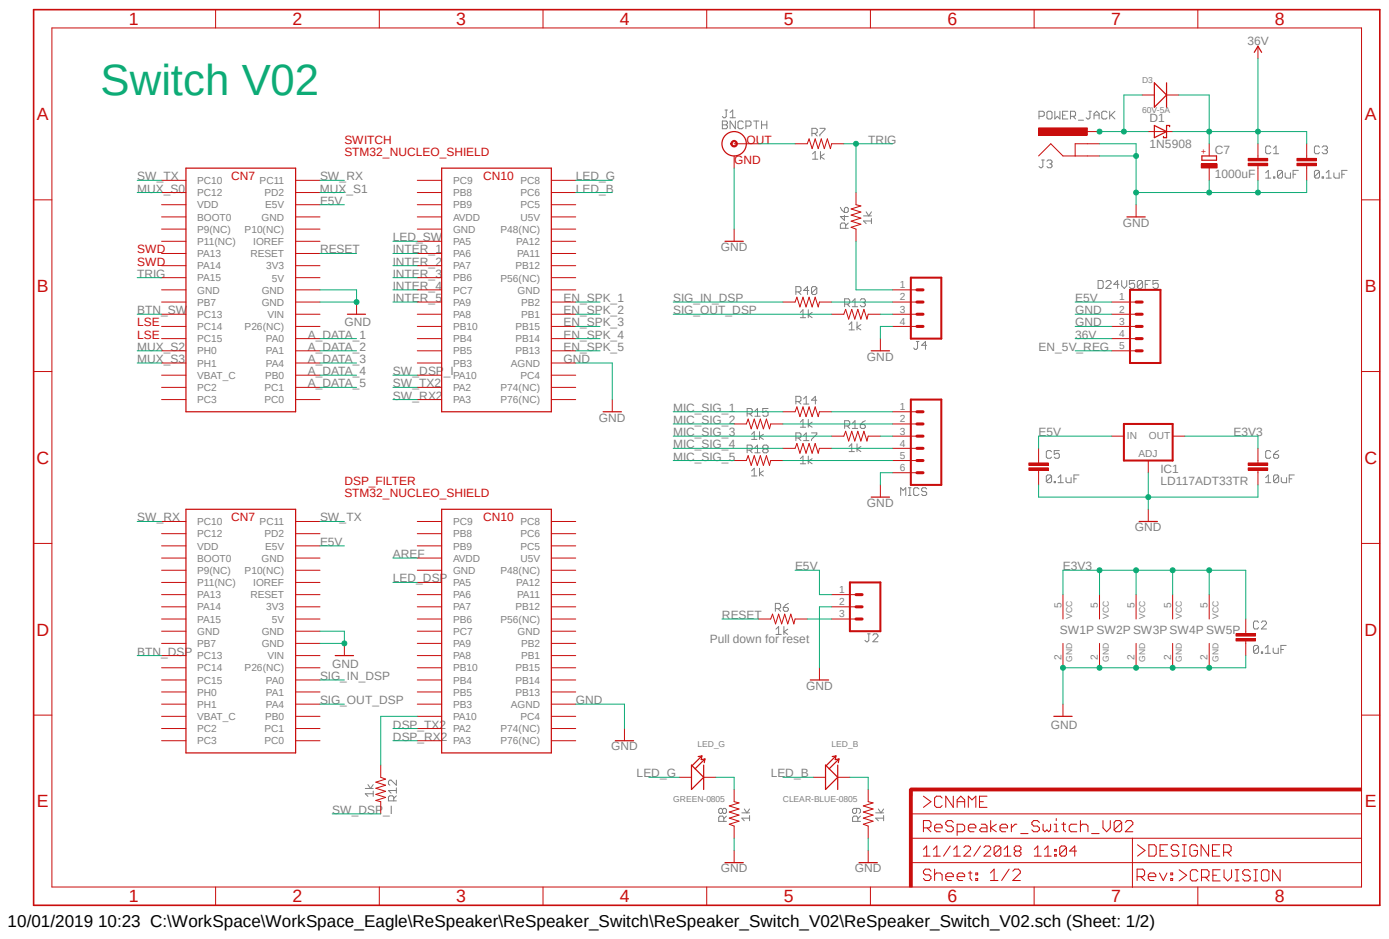
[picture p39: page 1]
GND; LD117ADT33TR; GREEN-0805; CLEAR-BLUE-0805 GND; VDD; BOOT0; IOREF; RESET; VIN; VBAT_C; AVDD; AGND; ADJ; IN OUTIC1; LED_G; LED_B; 6 GND GND; SIG_IN_DSP; SIG_OUT_DSP; BTN_DSP; LED_DSP; DSP_TX2 DSP_RX2; AREF; SW_DSP_I; A_DATA_1; EN_SPK_1; A_DATA_2 A_DATA_3 A_DATA_4 A_DATA_5; EN_SPK_2 EN_SPK_3 EN_SPK_4 EN_SPK_5; MUX_S0; MUX_S1; MUX_S2 MUX_S3; BTN_SW; LED_SW; 36V EN_5V_REG; INTER_1 INTER_2 INTER_3 INTER_4 INTER_5; TRIG; MIC_SIG_1 MIC_SIG_2 MIC_SIG_3 MIC_SIG_4 MIC_SIG_5; SWD; LSE LSE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

RESET
Pull down for reset

10/01/2019 10:23 C:\WorkSpace\WorkSpace_Eagle\ReSpeaker\ReSpeaker_Switch\ReSpeaker_Switch_V02\ReSpeaker_Switch_V02.sch (Sheet: 1/2)

# 5 SPK1

A

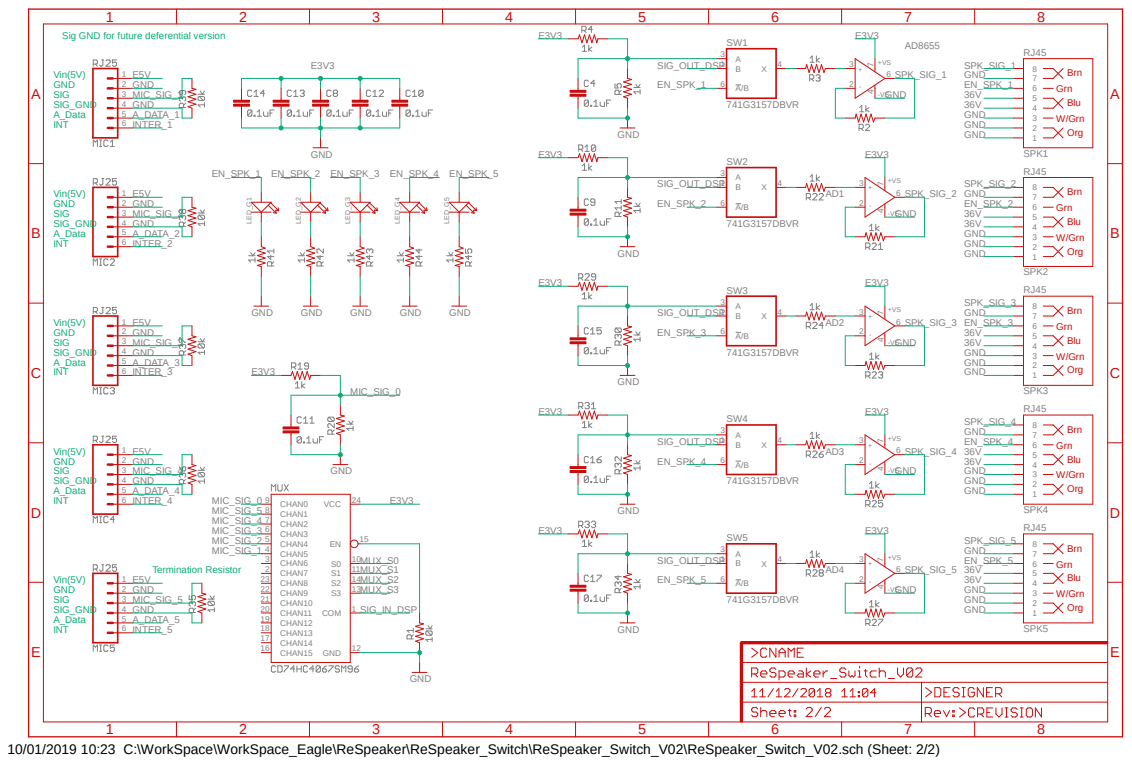
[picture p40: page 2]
741G3157DBVR; GND; -VS GND; COM; CHAN7 2; CHAN6 3; CHAN5 4; CHAN4 5; CHAN3 6; CHAN2 7; CHAN1 8; CHAN0 9; CHAN15 16; CHAN14 17; CHAN13 18; CHAN12 19; CHAN11 20; CHAN10 21; CHAN9 22; CHAN8 23; VCC; 8 7 6 5 SPK2; 8 7 6 5 SPK3; 8 7 6 5 SPK4; 8 7 6 5 SPK5; 6 4 7 AD4 LED_G¹; LED_G²; LED_G³; LED_G⁴; LED_G⁵; GND GND GND; SIG_IN_DSP; SIG_OUT_DSP; MIC_SIG_1; A_DATA_1 INTER_1; SPK_SIG_1; EN_SPK_1; MIC_SIG_2; A_DATA_2 INTER_2; MIC_SIG_3; A_DATA_3 INTER_3; MIC_SIG_4; A_DATA_4; INTER_4; MIC_SIG_0; MIC_SIG_5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

Sig GND for future deferential version

10/01/2019 10:23 C:\WorkSpace\WorkSpace_Eagle\ReSpeaker\ReSpeaker_Switch\ReSpeaker_Switch_V02\ReSpeaker_Switch_V02.sch (Sheet: 2/2)

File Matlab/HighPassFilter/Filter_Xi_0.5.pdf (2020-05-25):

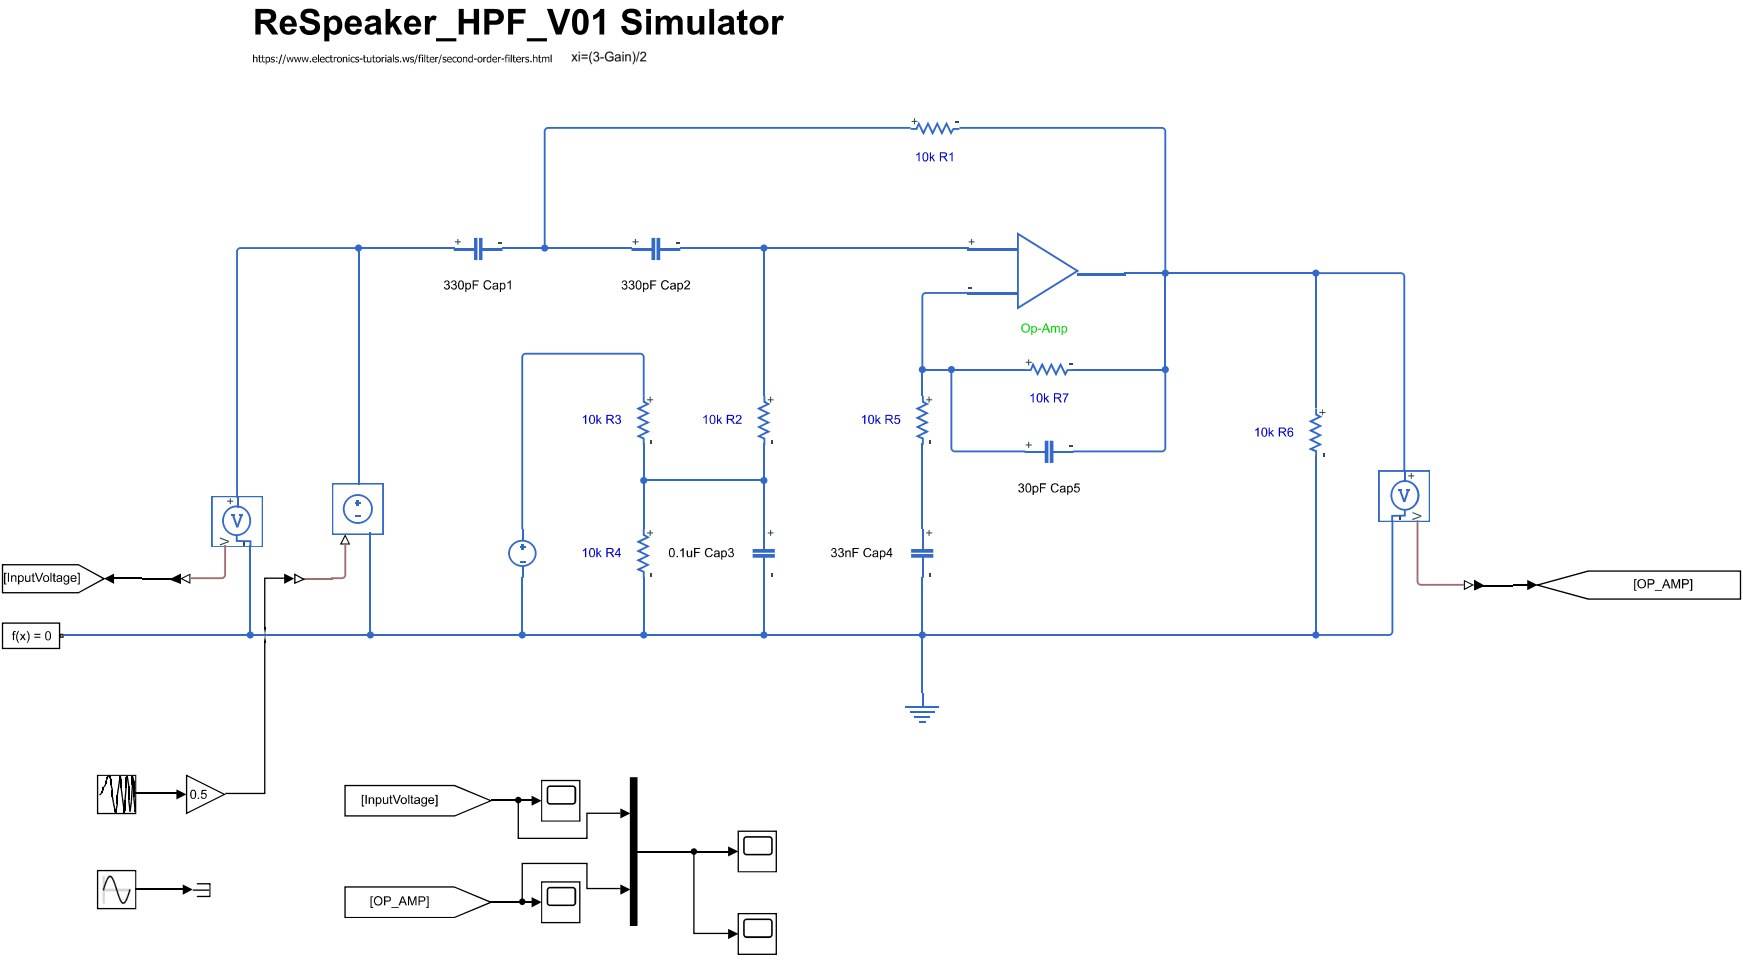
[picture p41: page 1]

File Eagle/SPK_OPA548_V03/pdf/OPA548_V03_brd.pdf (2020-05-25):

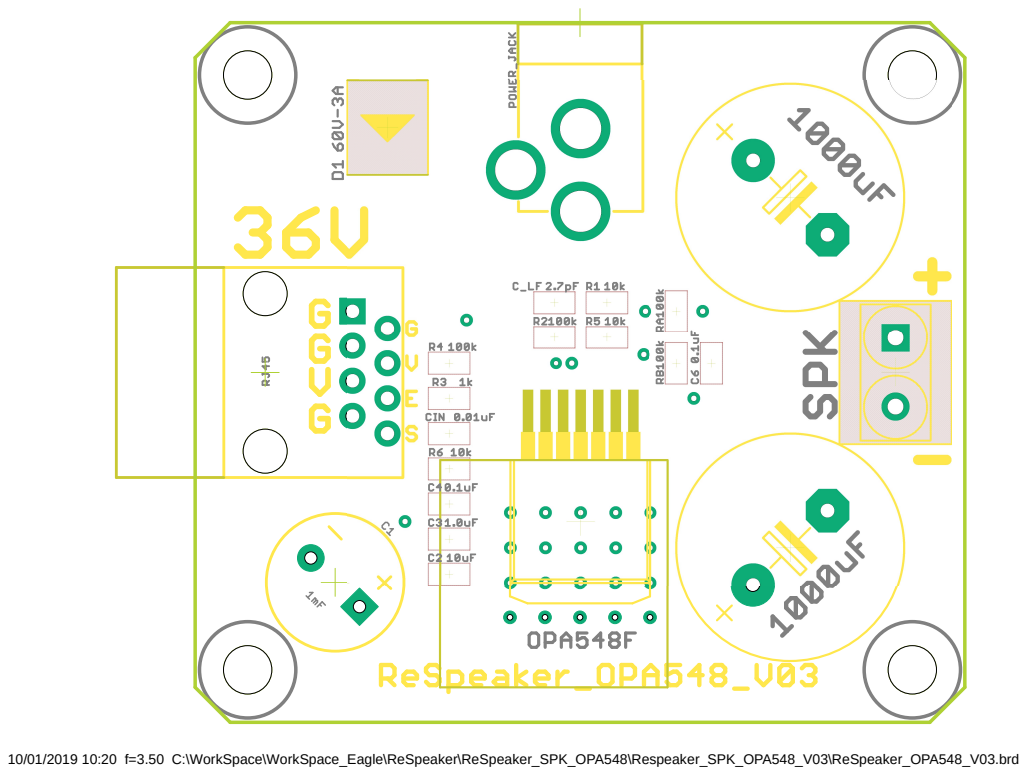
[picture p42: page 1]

10/01/2019 10:20 f=3.50 C:\WorkSpace\WorkSpace_Eagle\ReSpeaker\ReSpeaker_SPK_OPA548\Respeaker_SPK_OPA548_V03\ReSpeaker_OPA548_V03.brd

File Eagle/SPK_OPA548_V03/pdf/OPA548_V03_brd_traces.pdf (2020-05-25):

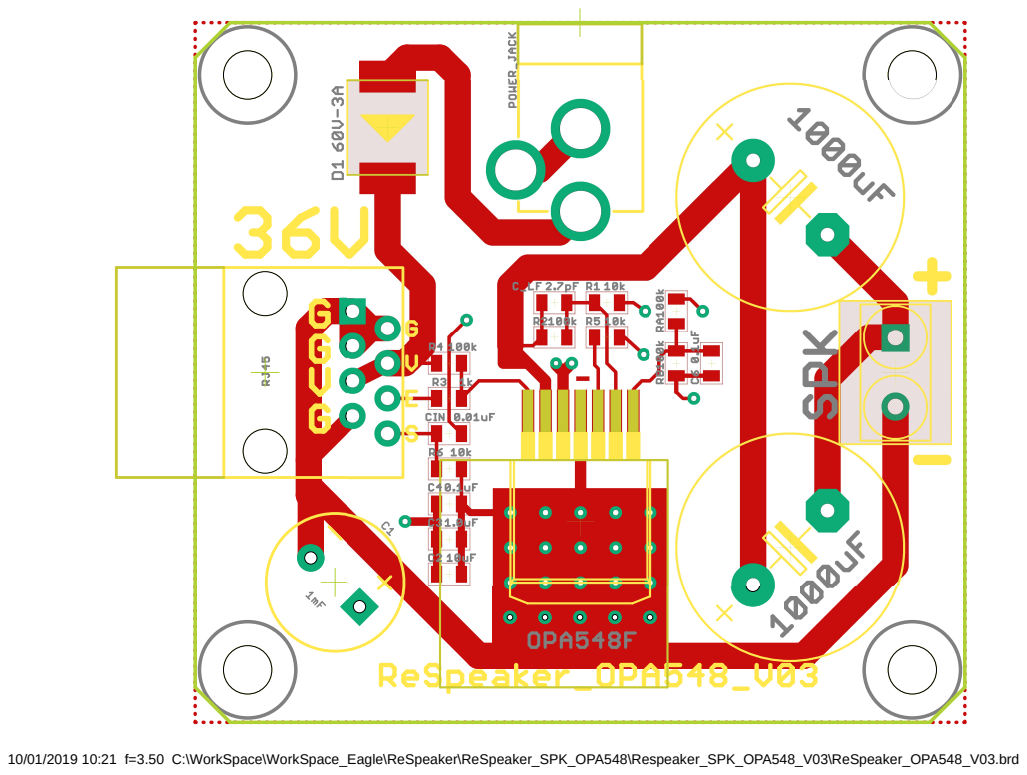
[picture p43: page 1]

10/01/2019 10:21 f=3.50 C:\WorkSpace\WorkSpace_Eagle\ReSpeaker\ReSpeaker_SPK_OPA548\Respeaker_SPK_OPA548_V03\ReSpeaker_OPA548_V03.brd

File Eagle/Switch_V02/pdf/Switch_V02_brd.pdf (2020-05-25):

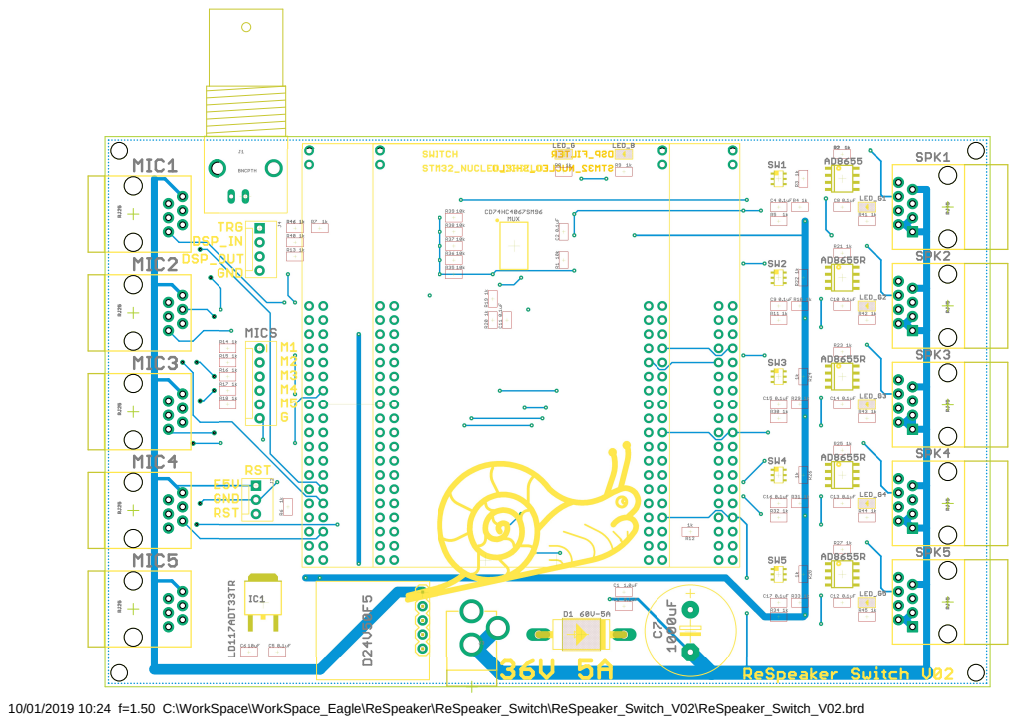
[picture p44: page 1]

10/01/2019 10:24 f=1.50 C:\WorkSpace\WorkSpace_Eagle\ReSpeaker\ReSpeaker_Switch\ReSpeaker_Switch_V02\ReSpeaker_Switch_V02.brd

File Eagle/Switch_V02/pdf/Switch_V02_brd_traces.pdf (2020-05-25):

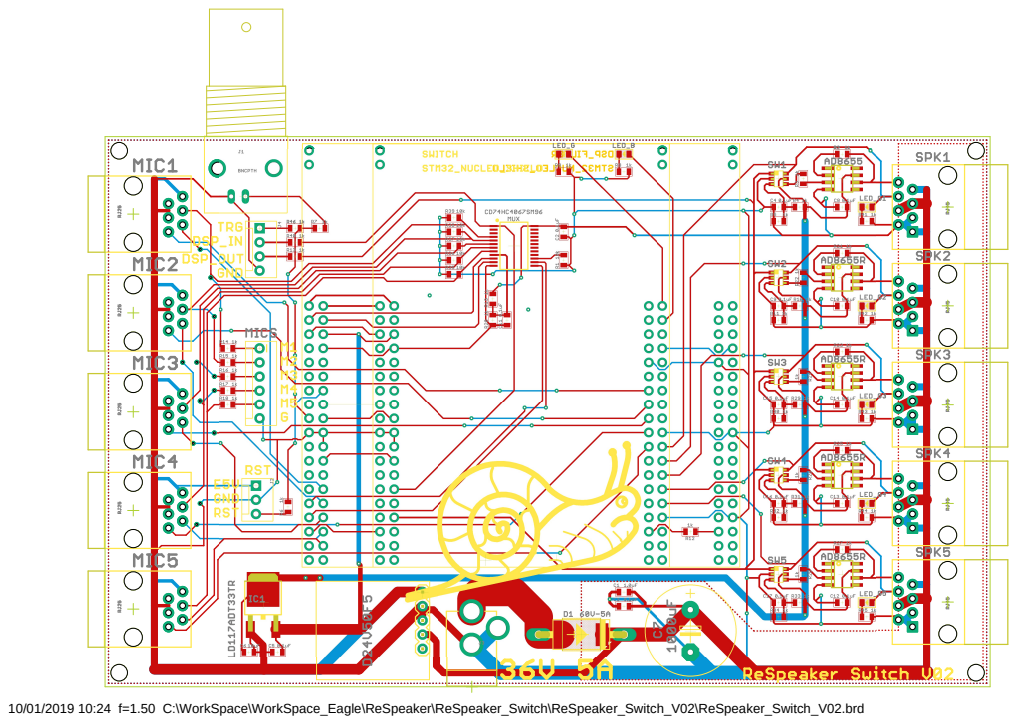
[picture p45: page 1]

10/01/2019 10:24 f=1.50 C:\WorkSpace\WorkSpace_Eagle\ReSpeaker\ReSpeaker_Switch\ReSpeaker_Switch_V02\ReSpeaker_Switch_V02.brd

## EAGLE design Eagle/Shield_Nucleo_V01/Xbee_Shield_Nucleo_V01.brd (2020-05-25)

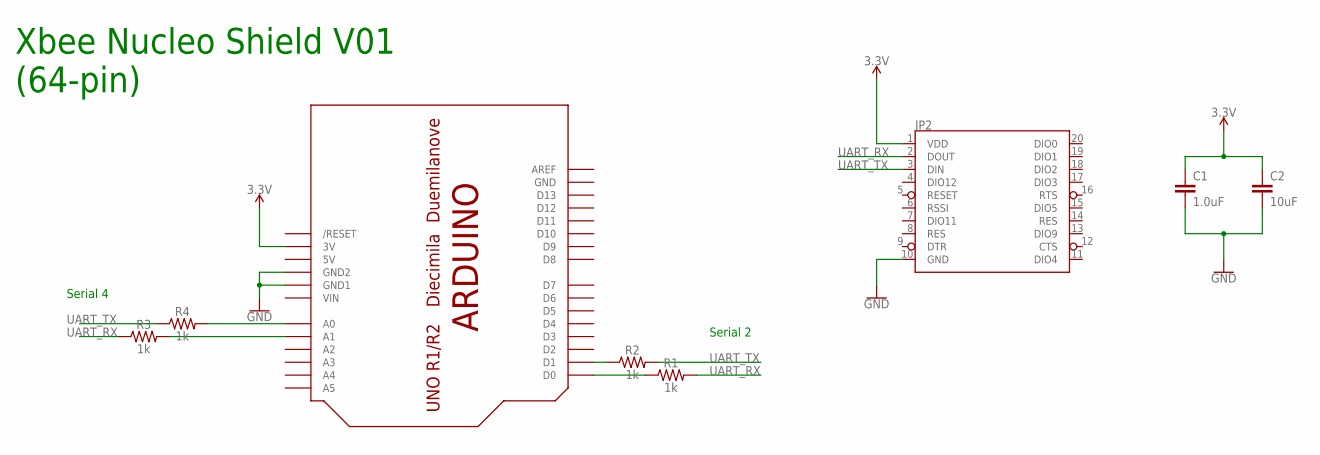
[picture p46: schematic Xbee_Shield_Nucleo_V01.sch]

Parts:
C1: 1.0uF; 0805
C2: 10uF; 0805
JP2: XBEESILK; XBEE-SILK
R1, R2, R3, R4: 1k; 0805
U1: ARDUINO-NOHOLE

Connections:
3.3V: C1.1, C2.1, JP2.1 (VDD), U1.3V
5V: U1.5V
GND: C1.2, C2.2, JP2.10 (GND), U1.GND, U1.GND1, U1.GND2
unnamed: R1.1, U1.D0
unnamed: R2.1, U1.D1
unnamed: R4.2, U1.A0
unnamed: R3.2, U1.A1
UART_RX: JP2.2 (DOUT), R1.2, R3.1
UART_TX: JP2.3 (DIN), R2.2, R4.1
VIN: U1.VIN

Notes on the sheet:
Xbee Nucleo Shield V01 (64-pin)
Serial 4
Serial 2

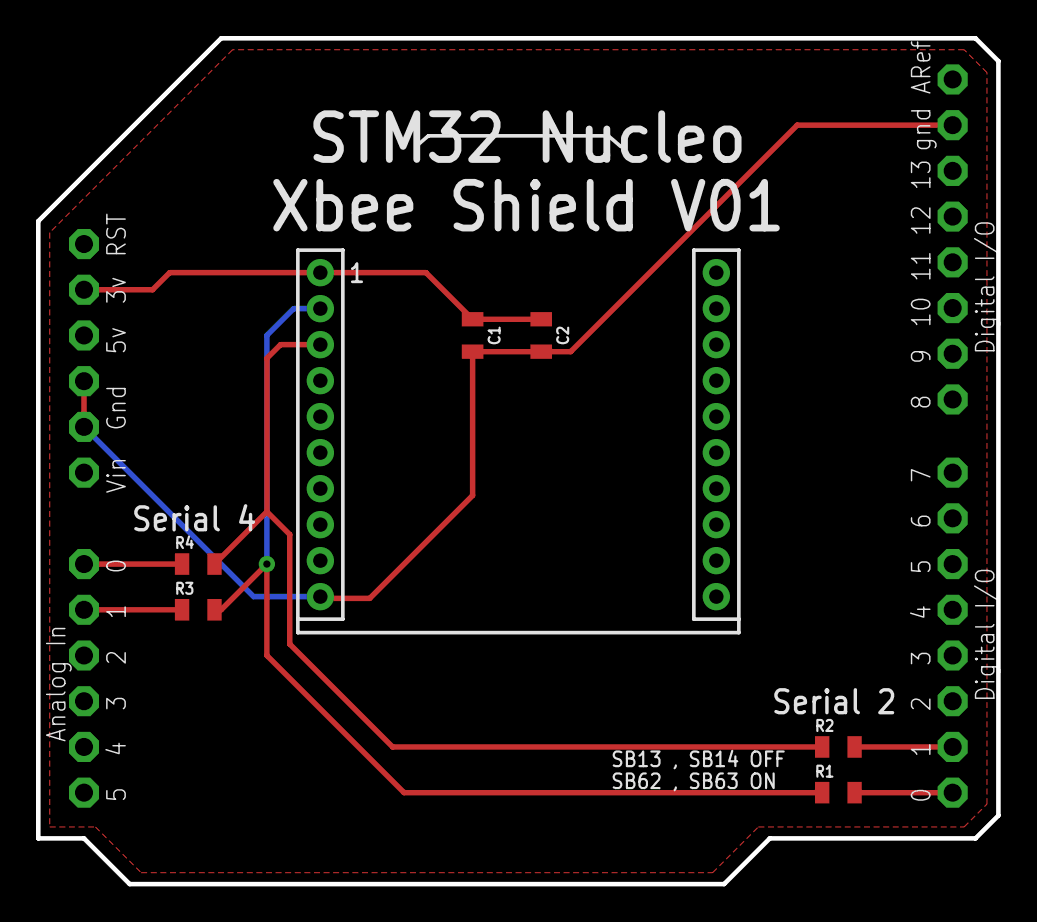
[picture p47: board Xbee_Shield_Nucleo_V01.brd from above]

Board: 2 copper layers, 53.3 x 47.0 mm, 8 parts (0 on the bottom side), 8 nets.

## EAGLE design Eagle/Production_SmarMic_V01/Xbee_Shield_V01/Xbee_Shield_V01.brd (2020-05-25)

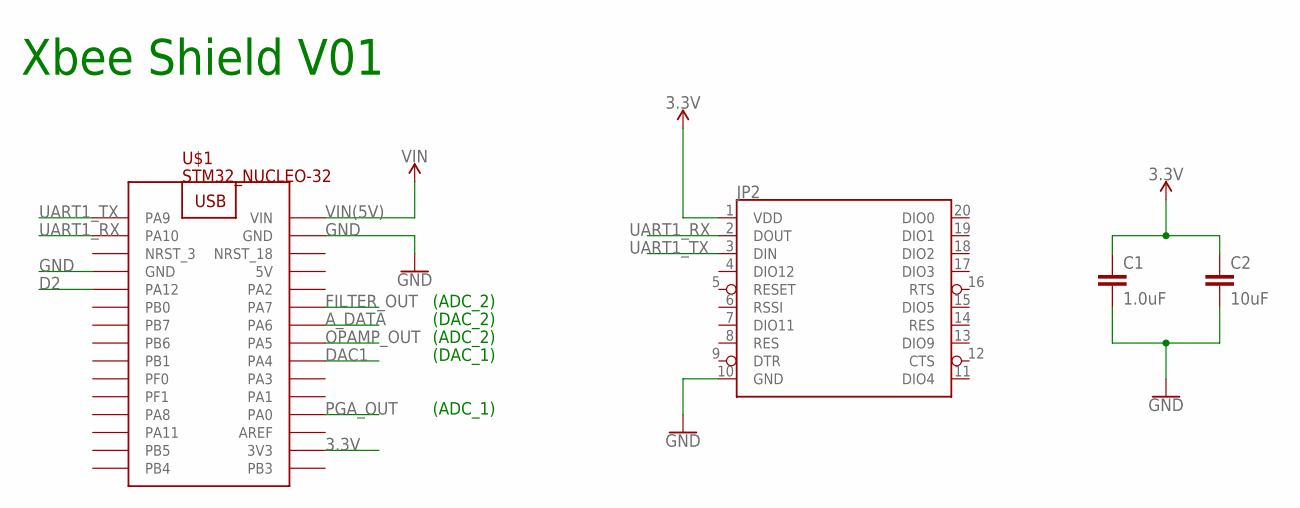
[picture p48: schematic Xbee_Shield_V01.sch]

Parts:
C1: 1.0uF; 0805
C2: 10uF; 0805
JP2: XBEESILK; XBEE-SILK
U$1: STM32_NUCLEO-32

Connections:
3.3V: C1.1, C2.1, JP2.1 (VDD), U$1.3V3
5V: U$1.5V
A_DATA: U$1.PA6
D2: U$1.PA12
DAC1: U$1.PA4
FILTER_OUT: U$1.PA7
GND: C1.2, C2.2, JP2.10 (GND), U$1.GND@4 (GND), U$1.GND@17 (GND)
OPAMP_OUT: U$1.PA5
PGA_OUT: U$1.PA0
UART1_RX: JP2.2 (DOUT), U$1.PA10
UART1_TX: JP2.3 (DIN), U$1.PA9
VIN(5V): U$1.VIN

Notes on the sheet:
Xbee Shield V01
(ADC_1)
(ADC_2)
(DAC_1)
(DAC_2)

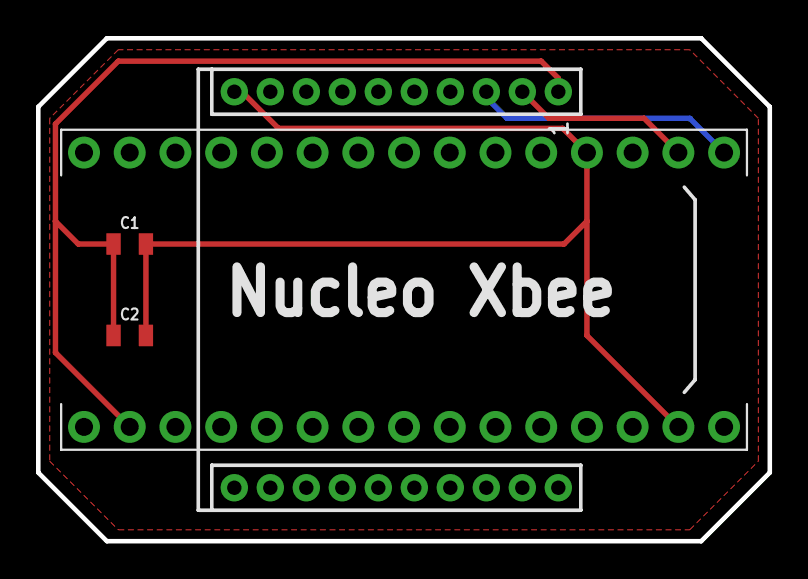
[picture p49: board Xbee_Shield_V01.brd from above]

Board: 2 copper layers, 40.6 x 27.9 mm, 4 parts (0 on the bottom side), 4 nets.

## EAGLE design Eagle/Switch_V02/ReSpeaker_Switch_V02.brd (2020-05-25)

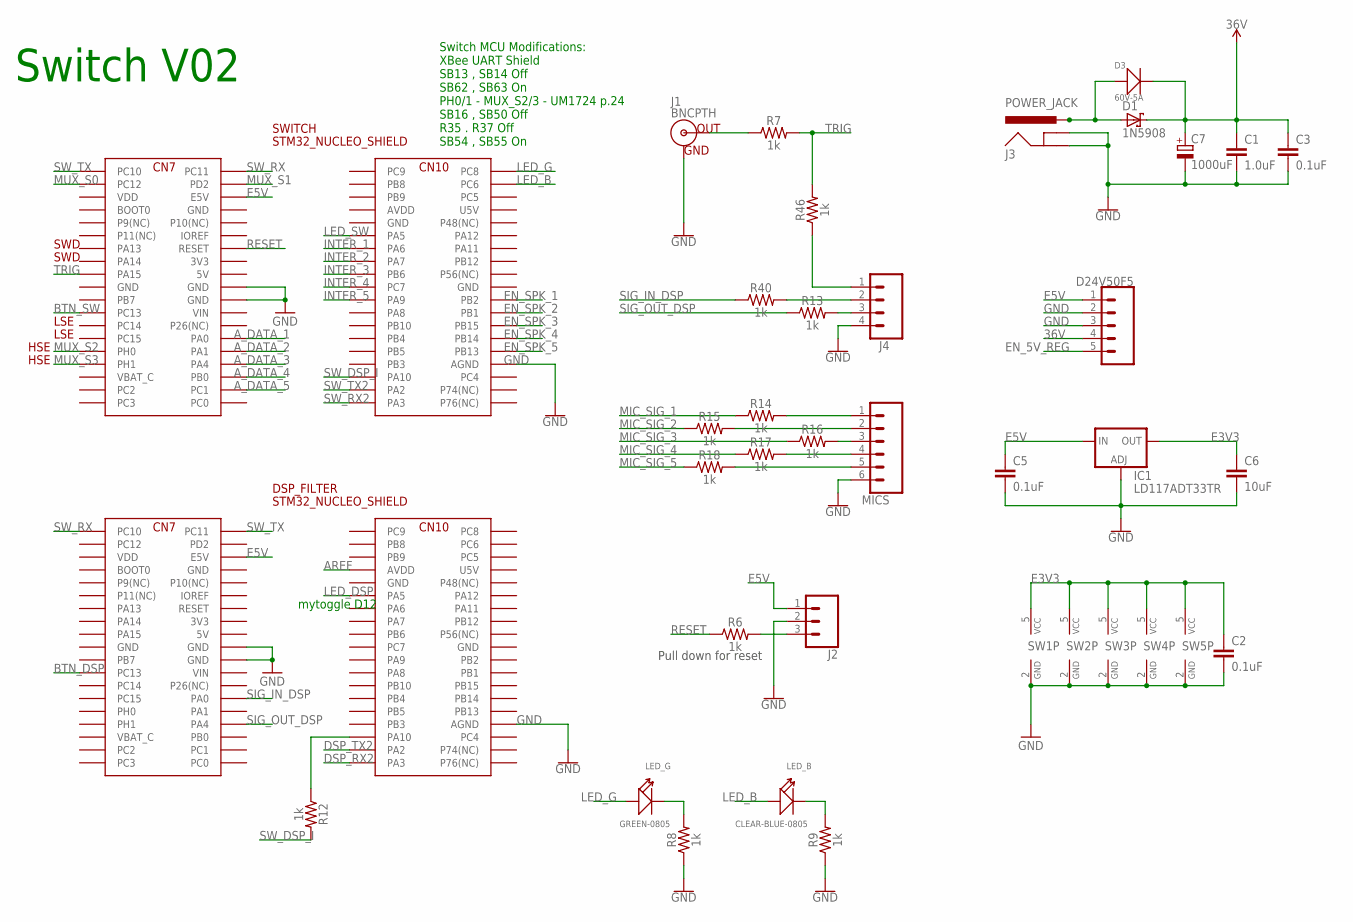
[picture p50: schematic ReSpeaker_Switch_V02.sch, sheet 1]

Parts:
C1: 1.0uF; 0805
C2, C3, C5: 0.1uF; 0805
C6: 10uF; 0805
C7: 1000uF; E7,5-16
D1: 1N5908; C4111-15
D3: 60V-5A; DO-214AB
D24V50F5: CONN_05; 1X05
DSP_FILTER: STM32_NUCLEO_SHIELD; STM32_NUCLEO
IC1: LD117ADT33TR; DPACK
J1: BNCPTH; BNC
J2: CONN_03POLAR; MOLEX-1X3
J3: POWER_JACK; POWER_JACK_PTH
J4: CONN_04POLAR; MOLEX-1X4
LED_B: CLEAR-BLUE-0805; LED-0805
LED_G: GREEN-0805; LED-0805
MICS: CONN_06POLAR; MOLEX-1X6
R6, R7, R8, R9, R12, R13, R14, R15, R16, R17, R18, R40, R46: 1k; 0805
SW1, SW2, SW3, SW4, SW5: 741G3157DBVR; DBV_R-PDSO-G6
SWITCH: STM32_NUCLEO_SHIELD; STM32_NUCLEO

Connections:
3V3: DSP_FILTER.3V3, SWITCH.3V3
5V: DSP_FILTER.5V, SWITCH.5V
36V: C1.1, C3.1, C7.+, D1.C, D3.2 (-), D24V50F5.4; also elsewhere on the board
AREF: DSP_FILTER.AVDD
AVDD: SWITCH.AVDD
A_DATA_1: SWITCH.PA0; also elsewhere on the board
A_DATA_2: SWITCH.PA1; also elsewhere on the board
A_DATA_3: SWITCH.PA4; also elsewhere on the board
A_DATA_4: SWITCH.PB0; also elsewhere on the board
A_DATA_5: SWITCH.PC1; also elsewhere on the board
BTN_DSP: DSP_FILTER.PC13
BTN_SW: SWITCH.PC13
DSP_RX2: DSP_FILTER.PA3
DSP_TX2: DSP_FILTER.PA2
E3V3: C2.1, C6.1, IC1.4 (OUT), SW1.5 (VCC), SW2.5 (VCC), SW3.5 (VCC), SW4.5 (VCC), SW5.5 (VCC); also elsewhere on the board
E5V: C5.1, D24V50F5.1, DSP_FILTER.E5V, IC1.3 (IN), J2.1, SWITCH.E5V; also elsewhere on the board
EN_5V_REG: D24V50F5.5
EN_SPK_1: SWITCH.PB2; also elsewhere on the board
EN_SPK_2: SWITCH.PB1; also elsewhere on the board
EN_SPK_3: SWITCH.PB15; also elsewhere on the board
EN_SPK_4: SWITCH.PB14; also elsewhere on the board
EN_SPK_5: SWITCH.PB13; also elsewhere on the board
GND: C1.2, C2.2, C3.2, C5.2, C6.2, C7.-, D24V50F5.2, D24V50F5.3, DSP_FILTER.AGND, DSP_FILTER.GND@8 (GND), DSP_FILTER.GND@19 (GND), DSP_FILTER.GND@20 (GND), DSP_FILTER.GND@22 (GND), DSP_FILTER.GND@47 (GND), DSP_FILTER.GND@58 (GND), IC1.1 (ADJ), J1.GND, J2.2, J3.GND, J3.GNDBREAK, J4.4, MICS.6, R8.1, R9.1, SW1.2 (GND), SW2.2 (GND), SW3.2 (GND), SW4.2 (GND), SW5.2 (GND), SWITCH.AGND, SWITCH.GND@8 (GND), SWITCH.GND@19 (GND), SWITCH.GND@20 (GND), SWITCH.GND@22 (GND), SWITCH.GND@47 (GND), SWITCH.GND@58 (GND); also elsewhere on the board
INTER_1: SWITCH.PA6; also elsewhere on the board
INTER_2: SWITCH.PA7; also elsewhere on the board
INTER_3: SWITCH.PB6; also elsewhere on the board
INTER_4: SWITCH.PC7; also elsewhere on the board
INTER_5: SWITCH.PA9; also elsewhere on the board
LED_B: LED_B.+, SWITCH.PC6
LED_DSP: DSP_FILTER.PA5
LED_G: LED_G.+, SWITCH.PC8
LED_SW: SWITCH.PA5
MIC_SIG_1: R14.1; also elsewhere on the board
MIC_SIG_2: R15.1; also elsewhere on the board
MIC_SIG_3: R16.1; also elsewhere on the board
MIC_SIG_4: R17.1; also elsewhere on the board
MIC_SIG_5: R18.1; also elsewhere on the board
MUX_S0: SWITCH.PC12; also elsewhere on the board
MUX_S1: SWITCH.PD2; also elsewhere on the board
MUX_S2: SWITCH.PH0; also elsewhere on the board
MUX_S3: SWITCH.PH1; also elsewhere on the board
unnamed: DSP_FILTER.PA10, R12.1
unnamed: D1.A, D3.1 (+), J3.PWR
unnamed: J1.S (OUT), R7.1
unnamed: J2.3, R6.2
unnamed: MICS.1, R14.2
unnamed: LED_G.-, R8.2
unnamed: LED_B.-, R9.2
unnamed: MICS.2, R15.2
unnamed: MICS.3, R16.2
unnamed: MICS.4, R17.2
unnamed: MICS.5, R18.2
unnamed: J4.2, R40.2
unnamed: J4.3, R13.2
unnamed: J4.1, R46.1
RESET: R6.1, SWITCH.RESET
SIG_IN_DSP: DSP_FILTER.PA0, R40.1; also elsewhere on the board
SIG_OUT_DSP: DSP_FILTER.PA4, R13.1; also elsewhere on the board
SW_DSP_I: R12.2, SWITCH.PA10
SW_RX: DSP_FILTER.PC10, SWITCH.PC11
SW_RX2: SWITCH.PA3
SW_TX: DSP_FILTER.PC11, SWITCH.PC10
SW_TX2: SWITCH.PA2
TRIG: R7.2, R46.2, SWITCH.PA15
U5V: DSP_FILTER.U5V, SWITCH.U5V
VBAT_C: DSP_FILTER.VBAT_C, SWITCH.VBAT_C
VDD: DSP_FILTER.VDD, SWITCH.VDD
VIN: DSP_FILTER.VIN, SWITCH.VIN

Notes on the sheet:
SWD
LSE
Switch V02
Pull down for reset
Switch MCU Modifications: XBee UART Shield SB13 , SB14 Off SB62 , SB63 On PH0/1 - MUX_S2/3 - UM1724 p.24 SB16 , SB50 Off R35 . R37 Off SB54 , SB55 On
HSE
mytoggle D12

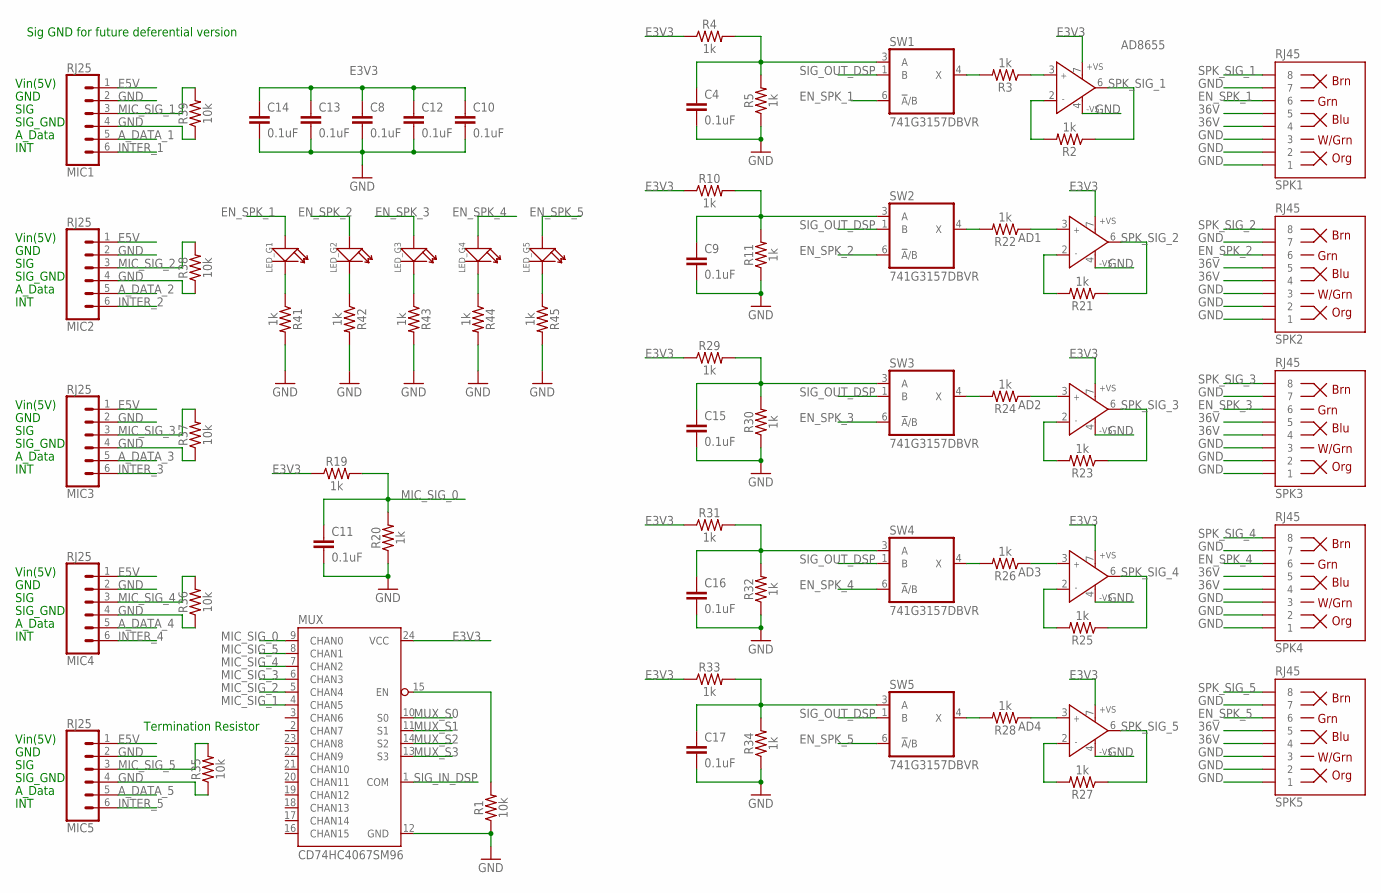
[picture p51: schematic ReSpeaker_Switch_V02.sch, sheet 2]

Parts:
AD1, AD2, AD3, AD4, AD8655: AD8655R; SO8
C4, C8, C9, C10, C11, C12, C13, C14, C15, C16, C17: 0.1uF; 0805
LED_G1, LED_G2, LED_G3, LED_G4, LED_G5: GREEN-0805; LED-0805
MIC1, MIC2, MIC3, MIC4, MIC5: RJ25; RJ11-6
MUX: CD74HC4067SM96; SSOP24
R1, R35, R36, R37, R38, R39: 10k; 0805
R2, R3, R4, R5, R10, R11, R19, R20, R21, R22, R23, R24, R25, R26, R27, R28, R29, R30, R31, R32, R33, R34, R41, R42, R43, R44, R45: 1k; 0805
SPK1, SPK2, SPK3, SPK4, SPK5: RJ45; RJ45-8
SW1, SW2, SW3, SW4, SW5: 741G3157DBVR; DBV_R-PDSO-G6

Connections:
36V: SPK1.4, SPK1.5, SPK2.4, SPK2.5, SPK3.4, SPK3.5, SPK4.4, SPK4.5, SPK5.4, SPK5.5; also elsewhere on the board
A_DATA_1: MIC1.5; also elsewhere on the board
A_DATA_2: MIC2.5; also elsewhere on the board
A_DATA_3: MIC3.5; also elsewhere on the board
A_DATA_4: MIC4.5; also elsewhere on the board
A_DATA_5: MIC5.5; also elsewhere on the board
E3V3: AD1.7 (+VS), AD2.7 (+VS), AD3.7 (+VS), AD4.7 (+VS), AD8655.7 (+VS), C8.1, C10.1, C12.1, C13.1, C14.1, MUX.24 (VCC), R4.1, R10.1, R19.1, R29.1, R31.1, R33.1; also elsewhere on the board
E5V: MIC1.1, MIC2.1, MIC3.1, MIC4.1, MIC5.1; also elsewhere on the board
EN_MUX: MUX.15 (EN), R1.2
EN_SPK_1: LED_G1.+, SPK1.6, SW1.6 (!A!/B); also elsewhere on the board
EN_SPK_2: LED_G2.+, SPK2.6, SW2.6 (!A!/B); also elsewhere on the board
EN_SPK_3: LED_G3.+, SPK3.6, SW3.6 (!A!/B); also elsewhere on the board
EN_SPK_4: LED_G4.+, SPK4.6, SW4.6 (!A!/B); also elsewhere on the board
EN_SPK_5: LED_G5.+, SPK5.6, SW5.6 (!A!/B); also elsewhere on the board
GND: AD1.4 (-VS), AD2.4 (-VS), AD3.4 (-VS), AD4.4 (-VS), AD8655.4 (-VS), C4.2, C8.2, C9.2, C10.2, C11.2, C12.2, C13.2, C14.2, C15.2, C16.2, C17.2, MIC1.2, MIC1.4, MIC2.2, MIC2.4, MIC3.2, MIC3.4, MIC4.2, MIC4.4, MIC5.2, MIC5.4, MUX.12 (GND), R1.1, R5.1, R11.1, R20.1, R30.1, R32.1, R34.1, R35.1, R36.1, R37.1, R38.1, R39.1, R41.2, R42.2, R43.2, R44.2, R45.2, SPK1.1, SPK1.2, SPK1.3, SPK1.7, SPK2.1, SPK2.2, SPK2.3, SPK2.7, SPK3.1, SPK3.2, SPK3.3, SPK3.7, SPK4.1, SPK4.2, SPK4.3, SPK4.7, SPK5.1, SPK5.2, SPK5.3, SPK5.7; also elsewhere on the board
INTER_1: MIC1.6; also elsewhere on the board
INTER_2: MIC2.6; also elsewhere on the board
INTER_3: MIC3.6; also elsewhere on the board
INTER_4: MIC4.6; also elsewhere on the board
INTER_5: MIC5.6; also elsewhere on the board
MIC_SIG_0: C11.1, MUX.9 (CHAN0), R19.2, R20.2
MIC_SIG_1: MIC1.3, MUX.4 (CHAN5), R39.2; also elsewhere on the board
MIC_SIG_2: MIC2.3, MUX.5 (CHAN4), R38.2; also elsewhere on the board
MIC_SIG_3: MIC3.3, MUX.6 (CHAN3), R37.2; also elsewhere on the board
MIC_SIG_4: MIC4.3, MUX.7 (CHAN2), R36.2; also elsewhere on the board
MIC_SIG_5: MIC5.3, MUX.8 (CHAN1), R35.2; also elsewhere on the board
MUX_S0: MUX.10 (S0); also elsewhere on the board
MUX_S1: MUX.11 (S1); also elsewhere on the board
MUX_S2: MUX.14 (S2); also elsewhere on the board
MUX_S3: MUX.13 (S3); also elsewhere on the board
unnamed: R3.2, SW1.4 (X)
unnamed: AD8655.3 (IN+), R3.1
unnamed: AD8655.2 (IN-), R2.2
unnamed: C4.1, R4.2, R5.2, SW1.3 (A)
unnamed: C9.1, R10.2, R11.2, SW2.3 (A)
unnamed: AD1.2 (IN-), R21.2
unnamed: AD2.2 (IN-), R23.2
unnamed: AD1.3 (IN+), R22.1
unnamed: AD2.3 (IN+), R24.1
unnamed: AD3.2 (IN-), R25.2
unnamed: AD3.3 (IN+), R26.1
unnamed: AD4.2 (IN-), R27.2
unnamed: AD4.3 (IN+), R28.1
unnamed: C15.1, R29.2, R30.2, SW3.3 (A)
unnamed: R22.2, SW2.4 (X)
unnamed: C16.1, R31.2, R32.2, SW4.3 (A)
unnamed: R24.2, SW3.4 (X)
unnamed: C17.1, R33.2, R34.2, SW5.3 (A)
unnamed: R26.2, SW4.4 (X)
unnamed: R28.2, SW5.4 (X)
unnamed: LED_G1.-, R41.1
unnamed: LED_G2.-, R42.1
unnamed: LED_G3.-, R43.1
unnamed: LED_G4.-, R44.1
unnamed: LED_G5.-, R45.1
SIG_IN_DSP: MUX.1 (COM); also elsewhere on the board
SIG_OUT_DSP: SW1.1 (B), SW2.1 (B), SW3.1 (B), SW4.1 (B), SW5.1 (B); also elsewhere on the board
SPK_SIG_1: AD8655.6 (OUT), R2.1, SPK1.8
SPK_SIG_2: AD1.6 (OUT), R21.1, SPK2.8
SPK_SIG_3: AD2.6 (OUT), R23.1, SPK3.8
SPK_SIG_4: AD3.6 (OUT), R25.1, SPK4.8
SPK_SIG_5: AD4.6 (OUT), R27.1, SPK5.8

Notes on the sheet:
SIG
SIG_GND
Vin(5V)
GND
A_Data
INT
Sig GND for future deferential version
Termination Resistor

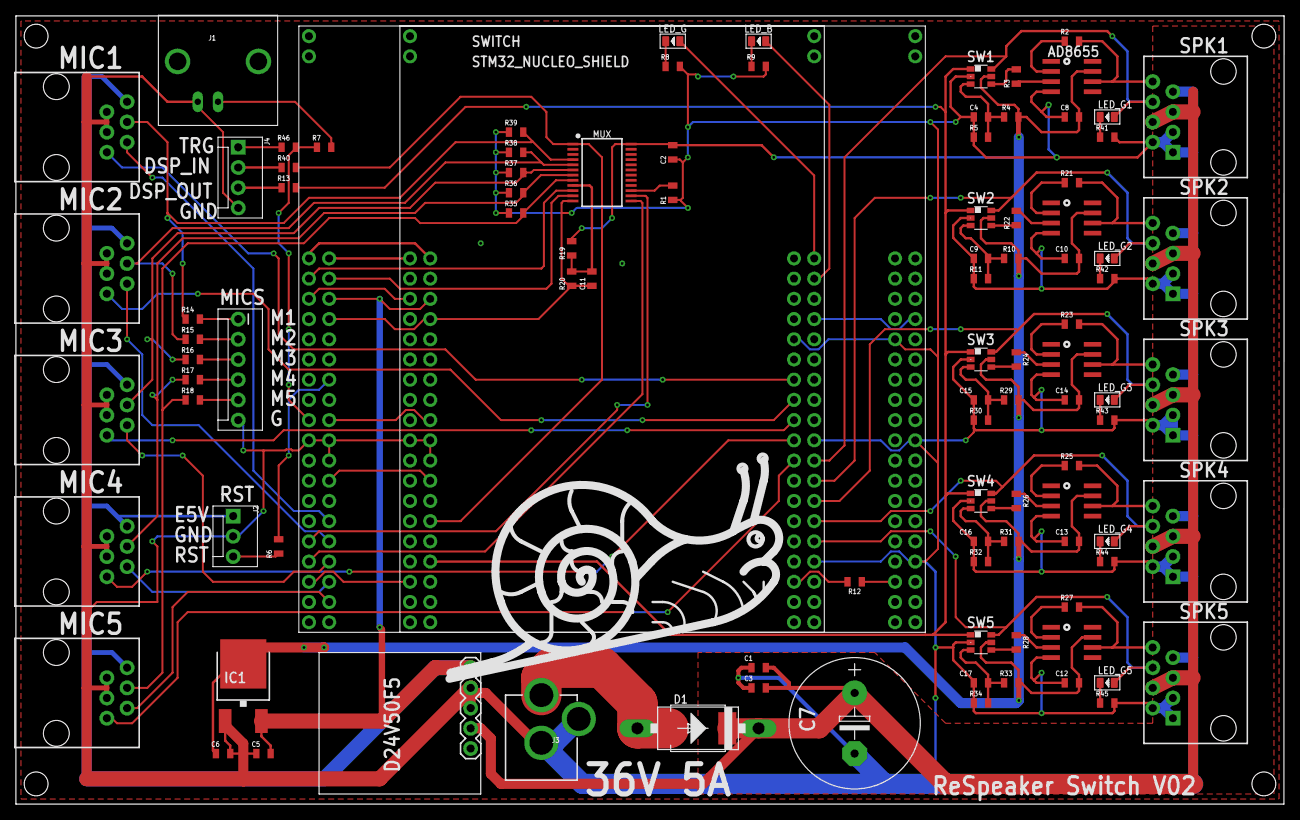
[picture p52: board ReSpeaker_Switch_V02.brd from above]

Board: 2 copper layers, 159.4 x 99.1 mm, 102 parts (0 on the bottom side), 89 nets.

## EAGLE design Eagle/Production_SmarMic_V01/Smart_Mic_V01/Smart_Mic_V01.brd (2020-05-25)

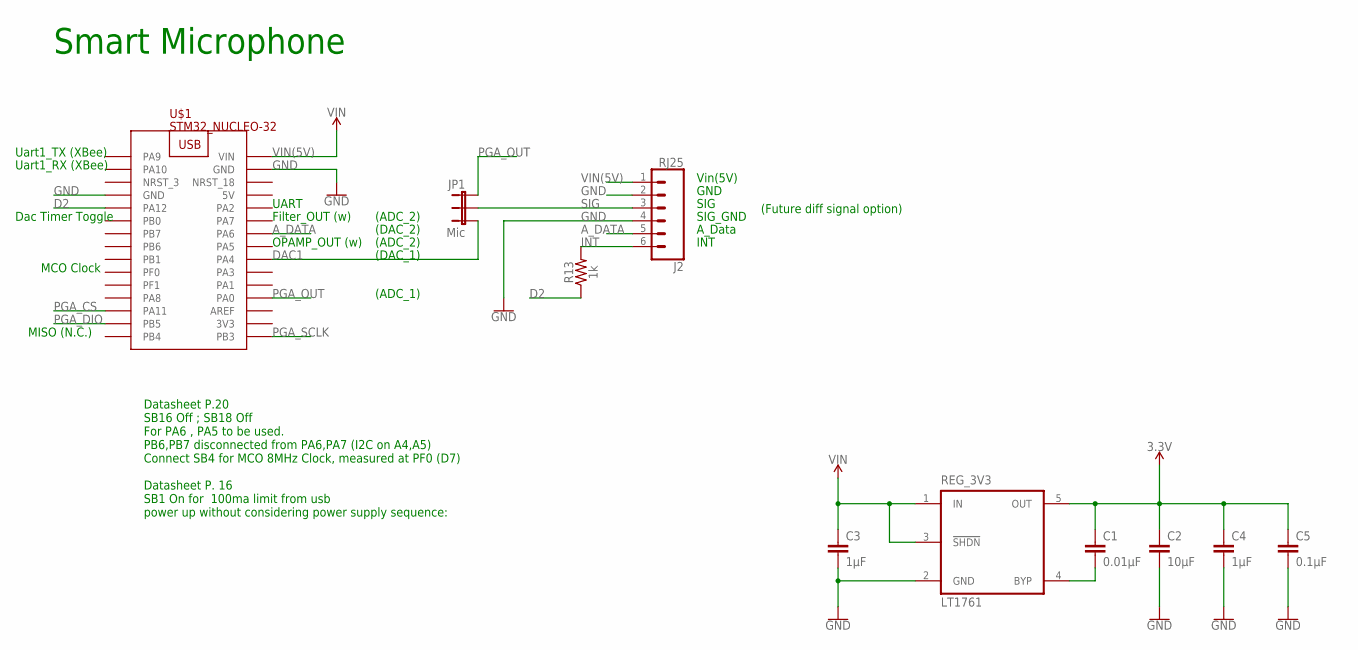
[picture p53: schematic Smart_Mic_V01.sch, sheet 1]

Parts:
C1: 0.01µF; 0805
C2: 10µF; 0805
C3, C4: 1µF; 0805
C5: 0.1µF; 0805
J2: RJ25; RJ11-6
JP1: Mic; 1X03
R13: 1k; 0805
REG_3V3: LT1761; SOT23-5
U$1: STM32_NUCLEO-32

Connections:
3.3V: C1.1, C2.1, C4.1, C5.1, REG_3V3.5 (OUT); also elsewhere on the board
3V3: U$1.3V3
5V: U$1.5V
A_DATA: J2.5, U$1.PA6
BYP: C1.2, REG_3V3.4 (BYP)
D2: R13.1, U$1.PA12
DAC1: JP1.3, U$1.PA4
GND: C2.2, C3.2, C4.2, C5.2, J2.2, J2.4, REG_3V3.2 (GND), U$1.GND@4 (GND), U$1.GND@17 (GND); also elsewhere on the board
INT: J2.6, R13.2
PGA_CS: U$1.PA11; also elsewhere on the board
PGA_DIO: U$1.PB5; also elsewhere on the board
PGA_OUT: JP1.1, U$1.PA0; also elsewhere on the board
PGA_SCLK: U$1.PB3; also elsewhere on the board
SIG: J2.3, JP1.2
VIN(5V): C3.1, J2.1, REG_3V3.1 (IN), REG_3V3.3 (!SHDN!), U$1.VIN

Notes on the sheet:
Smart Microphone
SIG
SIG_GND
Vin(5V)
GND
A_Data
INT
(Future diff signal option)
(ADC_1)
(ADC_2)
(DAC_1)
(DAC_2)
UART
Datasheet P.20 SB16 Off ; SB18 Off For PA6 , PA5 to be used. PB6,PB7 disconnected from PA6,PA7 (I2C on A4,A5) Connect SB4 for MCO 8MHz Clock, measured at PF0 (D7) Datasheet P. 16 SB1 On for 100ma limit from usb power up without considering power supply sequence:
MISO (N.C.)
OPAMP_OUT (w)
Filter_OUT (w)
Uart1_TX (XBee)
Uart1_RX (XBee)
MCO Clock
Dac Timer Toggle

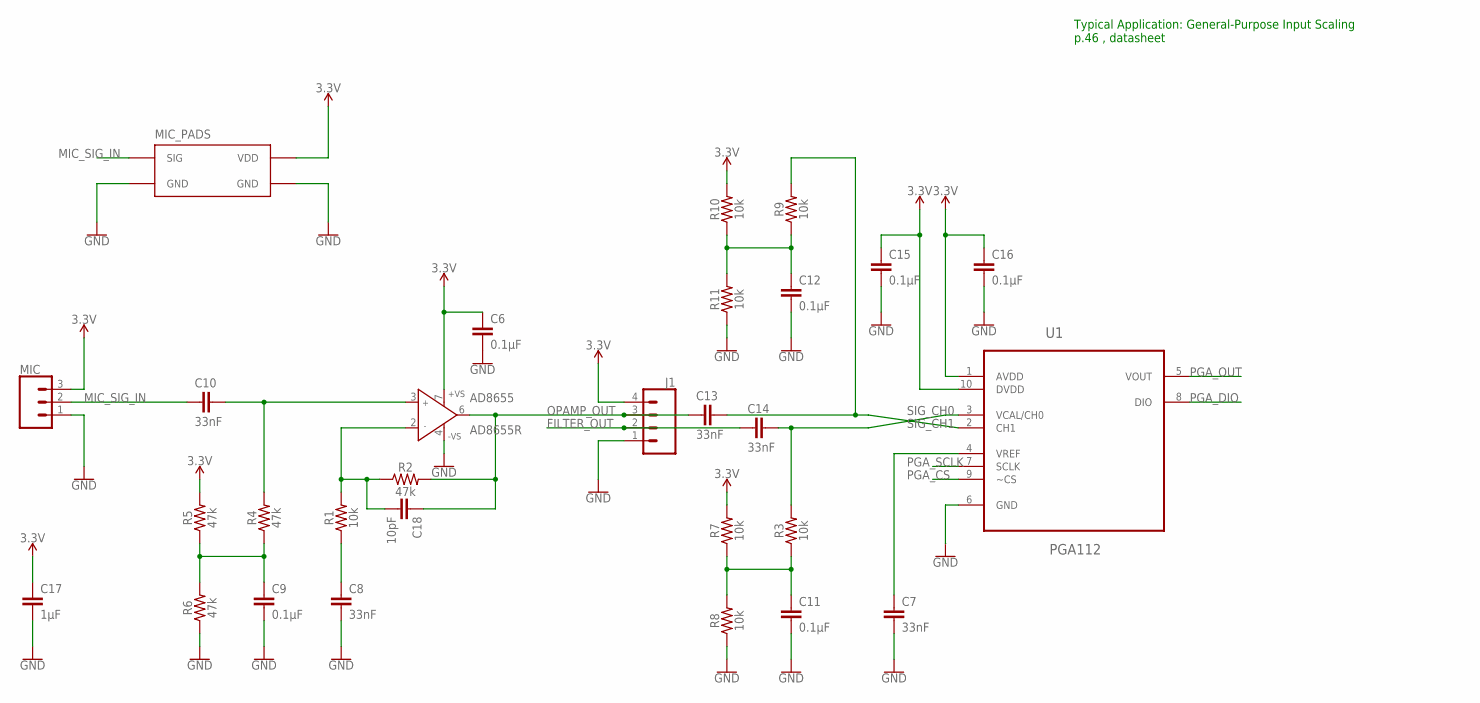
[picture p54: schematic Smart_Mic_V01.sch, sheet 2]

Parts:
AD8655: AD8655R; SO8
C6, C9, C11, C12, C15, C16: 0.1µF; 0805
C7, C8, C10, C13, C14: 33nF; 0805
C17: 1µF; 0805
C18: 10pF; 0805
J1: CONN_04; 1X04
MIC: CONN_03; 1X03
R1, R3, R7, R8, R9, R10, R11: 10k; 0805
R2, R4, R5, R6: 47k; 0805
U1: PGA112; SOP50P490X110-10N
U$2: MIC_PADS

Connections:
3.3V: AD8655.7 (+VS), C6.1, C15.1, C16.1, C17.1, J1.4, MIC.3, R5.2, R7.2, R10.2, U1.1 (AVDD), U1.10 (DVDD), U$2.VDD; also elsewhere on the board
FILTER_OUT: C14.2, J1.2
GND: AD8655.4 (-VS), C6.2, C7.2, C8.2, C9.2, C11.2, C12.2, C15.2, C16.2, C17.2, J1.1, MIC.1, R6.1, R8.1, R11.1, U1.6 (GND), U$2.GND$2 (GND), U$2.GND$4 (GND); also elsewhere on the board
MIC_SIG_IN: C10.2, MIC.2, U$2.SIG
unnamed: C7.1, U1.4 (VREF)
unnamed: C9.1, R4.1, R5.1, R6.2
unnamed: C11.1, R3.1, R7.1, R8.2
unnamed: C12.1, R9.1, R10.1, R11.2
unnamed: C8.1, R1.1
OP1_+: AD8655.3 (IN+), C10.1, R4.2
OP1_-: AD8655.2 (IN-), C18.2, R1.2, R2.1
OPAMP_OUT: AD8655.6 (OUT), C13.2, C18.1, J1.3, R2.2
PGA_CS: U1.9 (~CS); also elsewhere on the board
PGA_DIO: U1.8 (DIO); also elsewhere on the board
PGA_OUT: U1.5 (VOUT); also elsewhere on the board
PGA_SCLK: U1.7 (SCLK); also elsewhere on the board
SIG_CH0: C13.1, R9.2, U1.2 (CH1)
SIG_CH1: C14.1, R3.2, U1.3 (VCAL/CH0)

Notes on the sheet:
Typical Application: General-Purpose Input Scaling p.46 , datasheet

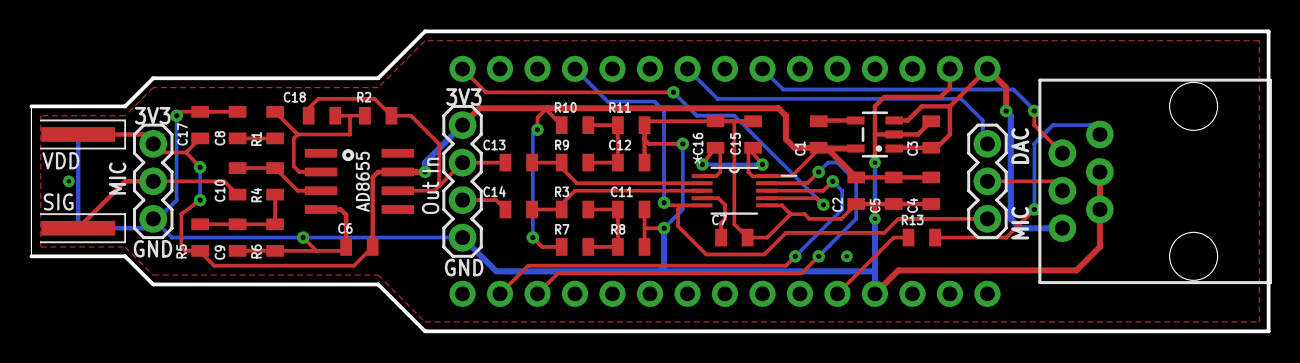
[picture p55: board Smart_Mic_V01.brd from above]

Board: 2 copper layers, 83.8 x 20.3 mm, 39 parts (1 on the bottom side), 25 nets.

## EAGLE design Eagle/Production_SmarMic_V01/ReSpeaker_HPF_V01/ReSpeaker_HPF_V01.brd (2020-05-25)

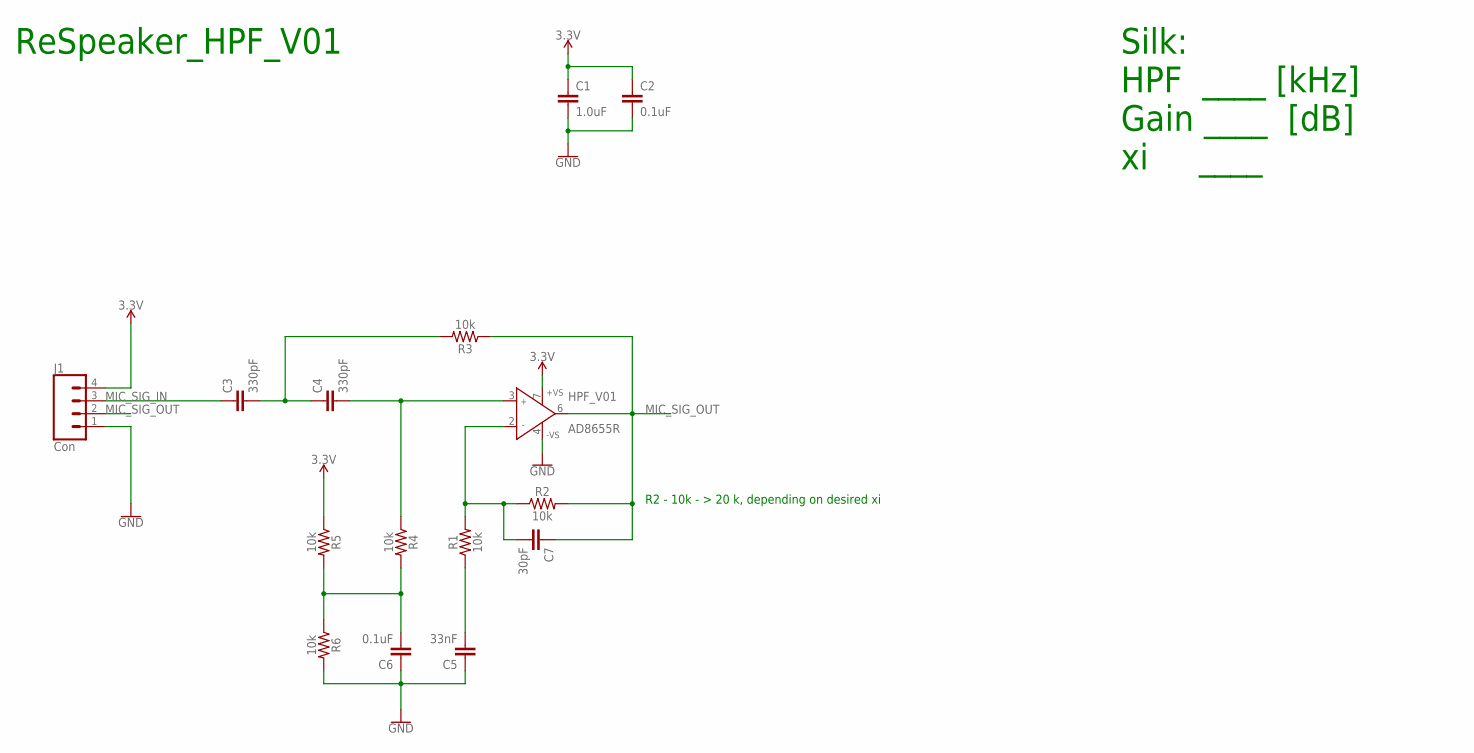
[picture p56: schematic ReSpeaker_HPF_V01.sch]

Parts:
C1: 1.0uF; 0805
C2, C6: 0.1uF; 0805
C3, C4: 330pF; 0805
C5: 33nF; 0805
C7: 30pF; 0805
HPF_V01: AD8655R; SO8
J1: Con; 1X04
R1, R2, R3, R4, R5, R6: 10k; 0805

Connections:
3.3V: C1.1, C2.1, HPF_V01.7 (+VS), J1.4, R5.1
GND: C1.2, C2.2, C5.1, C6.1, HPF_V01.4 (-VS), J1.1, R6.2
MIC_SIG_IN: C3.1, J1.3
MIC_SIG_OUT: C7.1, HPF_V01.6 (OUT), J1.2, R2.2, R3.1
unnamed: C3.2, C4.1, R3.2
unnamed: C4.2, HPF_V01.3 (IN+), R4.1
unnamed: C7.2, HPF_V01.2 (IN-), R1.2, R2.1
unnamed: C5.2, R1.1
unnamed: C6.2, R4.2, R5.2, R6.1

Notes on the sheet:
ReSpeaker_HPF_V01
R2 - 10k - > 20 k, depending on desired xi
Silk: HPF ____ [kHz] Gain ____ [dB] xi ____

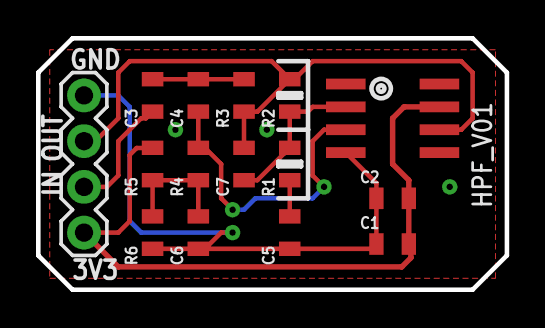
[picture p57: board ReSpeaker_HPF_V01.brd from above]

Board: 2 copper layers, 26.0 x 14.0 mm, 15 parts (0 on the bottom side), 9 nets.

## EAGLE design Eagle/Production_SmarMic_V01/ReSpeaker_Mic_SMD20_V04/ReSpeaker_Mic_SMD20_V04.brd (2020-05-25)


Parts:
C1: 33nF; 0805
J1: Mic_Sig; 1X02_2.0MM
J2: Mic_Supply; 1X02_2.0MM
_MIC_: 0.8; SPU0410LR5H-QB_0.8

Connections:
MIC_GND: C1.2, J1.2, J2.2, _MIC_.2 (GND), _MIC_.3 (GND), _MIC_.5 (GND), _MIC_.6 (GND)
MIC_OUT_CON: J1.1, _MIC_.1 (OUT)
MIC_VDD: C1.1, J2.1, _MIC_.4 (VDD)

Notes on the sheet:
ReSpeaker Microphone SMD V01


Board: 2 copper layers, 12.7 x 12.7 mm, 4 parts (0 on the bottom side), 3 nets.

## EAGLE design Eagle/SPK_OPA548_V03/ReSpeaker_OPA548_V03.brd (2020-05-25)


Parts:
C1: 1mF; CPOL-RADIAL-5MM-10MM
C2: 10uF; 0805
C3: 1.0uF; 0805
C4, C6: 0.1uF; 0805
C5, C7: 1000uF; E7,5-16
CIN: 0.01uF; 0805
C_LF: 2.7pF; 0805
D1: 60V-3A; DO-214AB
J1: RJ45; RJ45-8
J2: POWER_JACK; POWER_JACK_PTH
J3: SPK; H2-5.0-10.5X8.0MM
OPA1: OPA548F; DD-7
R1, R5, R6: 10k; 0805
R2, R4: 100k; 0805
R3: 1k; 0805
RA: 100k; 0805
RB: 100k; 0805

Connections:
36V: C1.+, C2.1, C3.1, C4.1, D1.2 (-), J1.4, J1.5, OPA1.5 (V+), R4.1, RA.2
EN_SPK: J1.6, R3.1
GND: C1.-, C2.2, C3.2, C4.2, C6.2, J1.1, J1.2, J1.3, J1.7, J2.GND, J2.GNDBREAK, J3.2, OPA1.4 (V-), R5.2, R6.1, RB.1
unnamed: D1.1 (+), J2.PWR
unnamed: C5.-, C7.-, J3.1
unnamed: CIN.2, R1.1
OPA_E.S: OPA1.7 (E/S), R3.2, R4.2
OPA_ILIM: OPA1.3 (ILIM), R5.1
OPA_IN+: C6.1, OPA1.1 (+IN), RA.1, RB.2
OPA_IN-: C_LF.1, OPA1.2 (-IN), R1.2, R2.1
OPA_OUT: C5.+, C7.+, C_LF.2, OPA1.6 (OUT), R2.2
SPK_SIG_IN: CIN.1, J1.8, R6.2

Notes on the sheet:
Notes: R5 Current limiter, rewired to GND CIN - Value changed to 0.01uf NOP_COG type. HPF=1/(2*pi*CIN*R1) ; --> 1.6Khz Filter capcitors 50V rating to support up to 36V operation voltage
COG
OpAmp Speaker OPA548 V03


Board: 2 copper layers, 55.9 x 50.8 mm, 22 parts (0 on the bottom side), 12 nets.

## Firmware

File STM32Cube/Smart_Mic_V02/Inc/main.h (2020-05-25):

/* USER CODE BEGIN Header */
/**
  ******************************************************************************
  * @file           : main.h
  * @brief          : Header for main.c file.
  *                   This file contains the common defines of the application.
  ******************************************************************************
  * @attention
  *
  * <h2><center>&copy; Copyright (c) 2019 STMicroelectronics.
  * All rights reserved.</center></h2>
  *
  * This software component is licensed by ST under BSD 3-Clause license,
  * the "License"; You may not use this file except in compliance with the
  * License. You may obtain a copy of the License at:
  *                        opensource.org/licenses/BSD-3-Clause
  *
  ******************************************************************************
  */
/* USER CODE END Header */

/* Define to prevent recursive inclusion -------------------------------------*/
#ifndef __MAIN_H
#define __MAIN_H

#ifdef __cplusplus
extern "C" {
#endif

/* Includes ------------------------------------------------------------------*/
#include "stm32l4xx_hal.h"

/* Private includes ----------------------------------------------------------*/
/* USER CODE BEGIN Includes */

/* USER CODE END Includes */

/* Exported types ------------------------------------------------------------*/
/* USER CODE BEGIN ET */

/* USER CODE END ET */

/* Exported constants --------------------------------------------------------*/
/* USER CODE BEGIN EC */

/* USER CODE END EC */

/* Exported macro ------------------------------------------------------------*/
/* USER CODE BEGIN EM */

/* USER CODE END EM */

/* Exported functions prototypes ---------------------------------------------*/
void Error_Handler(void);

/* USER CODE BEGIN EFP */

/* USER CODE END EFP */

/* Private defines -----------------------------------------------------------*/
#define PGA_OUT_Pin GPIO_PIN_0
#define PGA_OUT_GPIO_Port GPIOA
#define VCP_TX_Pin GPIO_PIN_2
#define VCP_TX_GPIO_Port GPIOA
#define MIC_OUT_Pin GPIO_PIN_4
#define MIC_OUT_GPIO_Port GPIOA
#define XBEE_TX_Pin GPIO_PIN_9
#define XBEE_TX_GPIO_Port GPIOA
#define XBEE_RX_Pin GPIO_PIN_10
#define XBEE_RX_GPIO_Port GPIOA
#define PGA_CS_Pin GPIO_PIN_11
#define PGA_CS_GPIO_Port GPIOA
#define D2_INT_Pin GPIO_PIN_12
#define D2_INT_GPIO_Port GPIOA
#define SWDIO_Pin GPIO_PIN_13
#define SWDIO_GPIO_Port GPIOA
#define SWCLK_Pin GPIO_PIN_14
#define SWCLK_GPIO_Port GPIOA
#define VCP_RX_Pin GPIO_PIN_15
#define VCP_RX_GPIO_Port GPIOA
#define PGA_SCK_Pin GPIO_PIN_3
#define PGA_SCK_GPIO_Port GPIOB
#define PGA_MOSI_Pin GPIO_PIN_5
#define PGA_MOSI_GPIO_Port GPIOB
/* USER CODE BEGIN Private defines */
#define MICNUM 1
#define PLAYBACK_MSG
//#define WIRELESS
//#define DEBUGGING_MSGS
//#ifdef
//#endif
/* USER CODE END Private defines */

#ifdef __cplusplus
}
#endif

#endif /* __MAIN_H */

/************************ (C) COPYRIGHT STMicroelectronics *****END OF FILE****/

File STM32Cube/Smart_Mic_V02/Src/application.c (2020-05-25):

/*
 * application.c
 *
 *  Created on: Mar 18, 2018
 *      Author: user
 */

/* Commands:
 * json:{"gain":0,"channel":0} // approximately 10ms to parse and send a response
 * json:{"threshOn":1000}
 * json:{"sigThresh":0.5} // range [0 - 1]
 * json:{"adcLatency":1000} // range [0 - (ADC_BUFFER_SIZE - 1)]
 * json:{"recordState":0} // debug state for sending recorded audio to PC [0,1]
 */
#include "application.h"
#include "main.h"
#include "stm32l4xx_hal.h"
#include <stdio.h>  /* sprintf */
#include <string.h> /* strlen */
#include <stdlib.h> /* atoi  */
#include "jsmn.h"
//#include "eeprom.h"

// variables:
uint16_t buffADC[ADC_BUFFER_SIZE] = { 0 };
uint16_t buffADC_index = 0;
uint16_t buffOut_index = 0;
uint16_t threshOnSet = THRESH_KEEP_ON;
uint16_t threshOn = 0;

// record play back state;
uint8_t recordState = 1;

// signal latency (maximum ADC_BUFFER_SIZE)
uint16_t adcLatency = 1000;

// signal trigger threshold
uint16_t sigThresh = SIG_THRESH;

// PGA settings
uint8_t pgaGain = 3;
uint8_t pgaChannel = 0;

/* Virtual address array*/
//uint16_t VirtAddVarTab[NB_OF_VAR] = {EE_threshOnSet_add, EE_adcLatency_add, EE_sigThresh_add, EE_pgaGain_add, EE_pgaChannel_add};



// UART status
__IO ITStatus UartReady = RESET;
// UART buffers
char messageSend[MSG_BUFFER_SIZE];
char messageRec[MSG_BUFFER_SIZE];

// UART interrupt buffers
uint8_t aRxBuffer[UART_RX_BUFFER_SIZE];
uint8_t aTxBuffer[UART_TX_BUFFER_SIZE] = " ";

// json buffer
char json[MSG_BUFFER_SIZE];
uint16_t jsonLength = 0;

// incoming packet
PacketMSG_struct packetMSG;

// functions
void setup_init(void) {
	// init PGA_CS pin to high (disable)
	HAL_GPIO_WritePin(PGA_CS_GPIO_Port, PGA_CS_Pin , GPIO_PIN_SET);
	HAL_Delay(100); // delay for PGA PowerUp
	// Init PGA SPI
	HAL_GPIO_WritePin(PGA_CS_GPIO_Port, PGA_CS_Pin , GPIO_PIN_RESET);
	uint16_t spiTransmit[1] = {0x0000};
	HAL_SPI_Transmit(&hspi3, (uint8_t*)spiTransmit, 1, 5000);
	HAL_GPIO_WritePin(PGA_CS_GPIO_Port, PGA_CS_Pin , GPIO_PIN_SET);

	// init adc / dac
	HAL_ADC_Start(&hadc1);
	HAL_DAC_Start(&hdac1, DAC_CHANNEL_1);

	// init dac register
	Dac1_Reg = (uint32_t) (hdac1.Instance);
	Dac1_Reg += DAC_DHR12R1_ALIGNMENT(DAC_ALIGN_12B_R);

	// initialize UART in interrupt mode
#ifdef WIRELESS
	if (HAL_UART_Receive_IT(&huart1, (uint8_t *) aRxBuffer, sizeof(aRxBuffer))
			!= HAL_OK) {
		Error_Handler();
	}
#else
	if (HAL_UART_Receive_IT(&huart2, (uint8_t *) aRxBuffer, sizeof(aRxBuffer))
			!= HAL_OK) {
		Error_Handler();
	}
#endif
	// set flag for waiting for incoming data
	UartReady = RESET;
}
//
//// initialize variables from eeprom
//void EE_setup_init (void){
//	// temp variables
//	uint16_t EE_temp_data = 0;
//
//	// update variables from eeprom
//	/* Unlock the Flash Program Erase controller */
//	HAL_FLASH_Unlock();
//
//	/* EEPROM Init */
//	EE_Init();
//
//	// read variables from EEPROM
//	EE_temp_data = threshOnSet;
//	EE_ReadVariable(EE_threshOnSet_add,  &EE_temp_data);
//	threshOnSet = EE_temp_data;
//
//	// read variables from EEPROM
//	EE_temp_data = adcLatency;
//	EE_ReadVariable(EE_adcLatency_add,  &EE_temp_data);
//	adcLatency = EE_temp_data;
//
//	// read variables from EEPROM
//	EE_temp_data = sigThresh;
//	EE_ReadVariable(EE_sigThresh_add,  &EE_temp_data);
//	sigThresh = EE_temp_data;
//
//	// read variables from EEPROM
//	EE_temp_data = (uint16_t) pgaGain;
//	EE_ReadVariable(EE_pgaGain_add,  &EE_temp_data);
//	pgaGain = (uint8_t) EE_temp_data;
//
//	// read variables from EEPROM
//	EE_temp_data = (uint16_t) pgaChannel;
//	EE_ReadVariable(EE_pgaChannel_add,  &EE_temp_data);
//	pgaChannel = (uint8_t) EE_temp_data;
//
//	// update PGA Settings
//	writePGA(pgaGain , pgaChannel);
//
//	/* Lock the Flash Program Erase controller */
//	//HAL_FLASH_Lock();
//}

/**
 * @brief  Rx Transfer completed callback
 * @param  UartHandle: UART handle
 * @note   This example shows a simple way to report end of DMA Rx transfer, and
 *         you can add your own implementation.
 * @retval None
 */


#ifdef WIRELESS
void HAL_UART_RxCpltCallback(UART_HandleTypeDef *huart1) {
	/* Set transmission flag: transfer complete */
	UartReady = SET;
}
#else
void HAL_UART_RxCpltCallback(UART_HandleTypeDef *huart2) {
	/* Set transmission flag: transfer complete */
	UartReady = SET;
}
#endif

// Serial Event function
void serialEvent(uint8_t inByte) {
	// detect start message , end message
	switch (packetMSG.syncFlag) {
	// waiting for header
	case 0: {
		if (packetMSG.header[packetMSG.syncIndex] == inByte) {
			packetMSG.syncIndex++;
			if (packetMSG.syncIndex == HEADER_SIZE) { // finish header SYNC
				packetMSG.syncFlag = 1; // start collecting data, wait for footer
				packetMSG.bufferIndex = 0;
				packetMSG.syncIndex = 0;
			}
		} else { // re-init sync
			packetMSG.syncIndex = 0;
		}
		//pc.printf("case 0 , %d  \r\n",packetMSG.syncIndex);
		break;
	}
	// waiting for footer
	case 1: {
		// add byte to buffer
		packetMSG.buffer[packetMSG.bufferIndex] = inByte;
		packetMSG.bufferIndex++;
		if (packetMSG.bufferIndex >= MSG_BUFFER_SIZE) { // buffer overflow
			// reset buffer
			packetMSG.bufferIndex = 0;
			packetMSG.syncIndex = 0;
			packetMSG.syncFlag = 0;
		} else if (packetMSG.footer[packetMSG.syncIndex] == inByte) { // footer char recieved
			packetMSG.syncIndex++;
			packetMSG.syncFlag = 2; // move to verify footer
		}
		//pc.printf("case 2 , %d  \r\n",packetMSG.syncIndex);
		break;
	}
	// verify footer
	case 2: {
		// add byte to buffer
		packetMSG.buffer[packetMSG.bufferIndex] = inByte;
		packetMSG.bufferIndex++;
		if (packetMSG.bufferIndex >= MSG_BUFFER_SIZE) { // buffer overflow
			// reset buffer
			packetMSG.bufferIndex = 0;
			packetMSG.syncIndex = 0;
			packetMSG.syncFlag = 0;
		} else if (packetMSG.footer[packetMSG.syncIndex] == inByte) { // footer char received
			packetMSG.syncIndex++;
			if (packetMSG.syncIndex == FOOTER_SIZE) { // finish footer SYNC
				packetMSG.syncFlag = 3;
				// copy packet to json buffer
				memcpy(&json, &packetMSG.buffer, packetMSG.bufferIndex);
				json[packetMSG.bufferIndex] = 0; //NULL; // end with NULL to indicate end of string
				jsonLength = packetMSG.bufferIndex;
				// send msg to parse.
				parsePacket();
				// reset buffer
				packetMSG.bufferIndex = 0;
				packetMSG.syncIndex = 0;
				packetMSG.syncFlag = 0;
			}
		} else { // footer broke restart wait for footer
			packetMSG.syncFlag = 1;
			// verify that it didn't broke on first footer char
			if (packetMSG.footer[0] == inByte) {
				packetMSG.syncIndex = 1;
			} else {
				packetMSG.syncIndex = 0;
			}
		}
		break;
	}
	default: {
		// something went wrong
		break;
	}
	} // end switch
} // end serialEvent

// compare to json tokens
int jsoneq(const char *json, jsmntok_t *tok, const char *s) {
	if (tok->type == JSMN_STRING && (int) strlen(s) == tok->end - tok->start
			&& strncmp(json + tok->start, s, tok->end - tok->start) == 0) {
		return 0;
	}
	return -1;
}

// Packet Parser
void parsePacket(void) {

	// send received message
	//HAL_UART_Transmit(&huart2, (uint8_t*) json, jsonLength, 5000); // send json packet
	// parse with JSMN parser
	int i;
	int r;
	jsmn_parser p;
	jsmntok_t t[20]; /* We expect no more than 128 tokens */

	jsmn_init(&p);
	r = jsmn_parse(&p, json, strlen(json), t, sizeof(t) / sizeof(t[0]));

	// test received  message
	//sprintf(messageSend, "r: %.d\r\n", r);
	//HAL_UART_Transmit(&huart2, (uint8_t*) messageSend, strlen(messageSend),5000);  // send json packet
	// verify root token is the specific mic
	if (jsoneq(json, &t[1], "mic") == 0) {
		// copy token into array - consider switching to strndup()
		char numString[10];
		sprintf(numString, "%.*s", t[2].end - t[2].start,json + t[2].start);
		int micAddr = atoi(numString);
#ifdef DEBUGGING_MSGS
		sprintf(messageSend, "micAddr: %d\r\n", micAddr);
		HAL_UART_Transmit(&huart2, (uint8_t*) messageSend,strlen(messageSend), 5000);  // send json packet
#endif
		// verify its the correct mic or the golden mic
		if ((micAddr == MICNUM) || (micAddr == 0)) {
			ackSend(1, MICNUM);
			/* Loop over all keys of the root object */
			for (i = 3; i < r; i++) {

				if (jsoneq(json, &t[i], "getSettings") == 0) {
					sprintf(messageSend, "{\"Settings\":%d,\"gain\":%d,\"channel\":%d,\"threshOn\":%d,\"sigThresh\":%d,\"adcLatency\":%d,\"recordState\":%d}\r\n"
							, MICNUM , pgaGain , pgaChannel , threshOnSet , sigThresh , adcLatency , recordState );
#ifdef WIRELESS
					HAL_UART_Transmit(&huart1, (uint8_t*) messageSend,strlen(messageSend), 5000);
					HAL_Delay(100); // allow xbee to finish packet
#else
					HAL_UART_Transmit(&huart2, (uint8_t*) messageSend,strlen(messageSend), 5000);
#endif

				}if (jsoneq(json, &t[i], "gain") == 0) {

					// copy token into array - consider switching to strndup()
					char numString[10];
					sprintf(numString, "%.*s", t[i + 1].end - t[i + 1].start,json + t[i + 1].start);
					pgaGain = atoi(numString);
					//EE_WriteVariable(EE_pgaGain_add,  (uint16_t)pgaGain);
#ifdef DEBUGGING_MSGS
					sprintf(messageSend, "pgaGain: %d\r\n", pgaGain);
					HAL_UART_Transmit(&huart2, (uint8_t*) messageSend,strlen(messageSend), 5000);  // send json packet
#endif
					// update PGA Settings
					writePGA(pgaGain , pgaChannel);

					i++;
				}else if (jsoneq(json, &t[i], "channel") == 0) {

					// copy token into array - consider switching to strndup()
					char numString[10];
					sprintf(numString, "%.*s", t[i + 1].end - t[i + 1].start,json + t[i + 1].start);
					pgaChannel = atoi(numString);
					//EE_WriteVariable(EE_pgaChannel_add,  (uint16_t)pgaChannel);
#ifdef DEBUGGING_MSGS
					sprintf(messageSend, "pgaChannel: %d\r\n", pgaChannel);
					HAL_UART_Transmit(&huart2, (uint8_t*) messageSend,strlen(messageSend), 5000);  // send json packet
#endif
					// update PGA Settings
					writePGA(pgaGain , pgaChannel);

					i++;
				}else if (jsoneq(json, &t[i], "threshOn") == 0) {

					// copy token into array - consider switching to strndup()
					char numString[10];
					sprintf(numString, "%.*s", t[i + 1].end - t[i + 1].start,json + t[i + 1].start);
					threshOnSet = atoi(numString);
					//EE_WriteVariable(EE_threshOnSet_add,  (uint16_t)threshOnSet);
#ifdef DEBUGGING_MSGS
					sprintf(messageSend, "threshOnSet: %d \r\n", (int)threshOnSet);
					HAL_UART_Transmit(&huart2, (uint8_t*) messageSend,strlen(messageSend), 5000);  // send json packet
#endif
					i++;
				}else if (jsoneq(json, &t[i], "sigThresh") == 0) {

					// copy token into array - consider switching to strndup()
					char numString[10];
					sprintf(numString, "%.*s", t[i + 1].end - t[i + 1].start,json + t[i + 1].start);
					float sigThreshFloat = atof(numString);
					if (sigThreshFloat>1) sigThreshFloat=1;
					if (sigThreshFloat<0) sigThreshFloat=0;
					sigThresh = (uint16_t) ( ((sigThreshFloat) * 4095/2) + 4095/2);
					//EE_WriteVariable(EE_sigThresh_add,  (uint16_t)sigThresh);
#ifdef DEBUGGING_MSGS
					sprintf(messageSend, "sigThresh: %d \r\n", (int)sigThresh);
					HAL_UART_Transmit(&huart2, (uint8_t*) messageSend,strlen(messageSend), 5000);  // send json packet
#endif
					i++;
				}else if (jsoneq(json, &t[i], "adcLatency") == 0) {

					// copy token into array - consider switching to strndup()
					char numString[10];
					sprintf(numString, "%.*s", t[i + 1].end - t[i + 1].start,json + t[i + 1].start);
					adcLatency = atoi(numString);
					if (adcLatency>=ADC_BUFFER_SIZE) adcLatency = (ADC_BUFFER_SIZE - 1);
					if (adcLatency<0) adcLatency = 0; // no latency
					//EE_WriteVariable(EE_adcLatency_add,  (uint16_t)adcLatency);
#ifdef DEBUGGING_MSGS
					sprintf(messageSend, "adcLatency: %d \r\n", (int)adcLatency);
					HAL_UART_Transmit(&huart2, (uint8_t*) messageSend,strlen(messageSend), 5000);  // send json packet
#endif
					i++;
				}else if (jsoneq(json, &t[i], "recordState") == 0) {
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

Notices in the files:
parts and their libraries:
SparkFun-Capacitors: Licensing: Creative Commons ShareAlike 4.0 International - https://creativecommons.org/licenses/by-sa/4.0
